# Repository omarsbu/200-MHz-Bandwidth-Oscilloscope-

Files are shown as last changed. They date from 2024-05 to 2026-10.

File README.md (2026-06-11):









**This project is intended to be an improvement on a previous version that can be seen here:**
https://github.com/omarsbu/1MHz-Bandwidth-Oscilloscope/tree/main/100kHz%20Oscilloscope

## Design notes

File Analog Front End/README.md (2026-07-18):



The purpose of an analog front end is to condition the input signal so that it maximizes the ADC’s dynamic range and limits the bandwidth to the ADC’s Nyquist frequency. Attenuators extend the measurable range by scaling down large input signals to within the appropriate voltage range and a programmable gain amplifier boosts small signals so they make full use of the ADC’s resolution. DC offsetting is also applied to bias the signal so that it fits well within the ADC’s input range. A high impedance JFET LNA buffer allows the oscilloscope input to be terminated with 1 MΩ or 50 Ω impedance.



The input stage of each channel consists of a set of relay switches to select between AC and DC coupling, as well as different attenuation levels. A compensated 1 MΩ L-pad attenuator is used for normal measurements with standard probes, while 50 Ω pi-attenuators are used for high-fidelity measurements from a 50 Ω source. Protection diodes clamp the input voltage if it exceeds the positive or negative supply rails.



The BUF802 is used in conjunction with the OPA140 to form a composite amplifier that delivers strong performance at both high and low frequencies. The BUF802, with its JFET input, provides exceptional AC performance but poor DC precision, while the OPA140 offers excellent DC precision but lacks sufficient bandwidth and slew rate for high-frequency signals. To leverage the strengths of both, the main input is AC-coupled to the BUF802, while the auxiliary input is driven by the OPA140’s DC offset circuitry. This circuitry uses a differential amplifier along with a DAC (0–5 V) and a 2.5 V reference to shift the output within a programmable range of ±2.5 V. A resistor in series with the differential amplifier output allows the DAC to modify the DC feedback network to the OPA140, which drives the BUF802 auxiliary input, thereby enabling a programmable DC offset of the input signal. To prevent the BUF802 output from exceeding the ±1 V differential input range of the LMH6518, Zener diodes are used to clamp the output to ±1 V. Additionally, a 50 Ω series resistor allows the BUF802 to drive the subsequent stages of the analog front-end signal chain as a 50 Ω source.



The ideal input condition of the LMH6518 are shown below:

The LMH6552 functions as a level shifter and single-ended to differential converter with 0 dB gain, providing a balanced differential input with a 2.5 V common-mode voltage to the LMH6518. The single-ended input to the LMH6552 is clamped to ±1 V by the BUF802, ensuring that the LMH6552’s differential output is also limited to ±1 V. The LMH6518 includes programmable bandwidth-limiting filters for anti-aliasing, and its output common-mode voltage is set to match the ADC’s common-mode voltage.









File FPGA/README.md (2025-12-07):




**Firmware Demo (Text is hard-coded for now)**



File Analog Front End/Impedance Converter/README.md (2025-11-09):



=> Impedance Converter serves as a buffer, presenting a 50GΩ input impedance and a driving the output with 50Ω output impedance. 

=> Large input impedance allows input impedance to be terminated with 1MΩ or 50Ω.

=> Composite amplifier formed with OPA140 which has high DC precision and BUF802 which has high superior AC performance. 

=> Differential Amplifier to offset output DC voltage by +/- 2.5V

=> Level shifter to drive LMH6518 with its ideal common-mode input voltage level for best performance.

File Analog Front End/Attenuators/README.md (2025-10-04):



=> Attenuators increase the input range of the scope by allowing signals with large amplitudes to be scaled down to within the ADC input range. 

=> Input range is reduced in 50 ohm mode due to larger power dissipation in the resistors. Higher power resistors can be used to increase the input range, however, physically larger resistors will have larger parasitics, which reduces high frequency performance of the 50 ohm path, which what it is intended for.







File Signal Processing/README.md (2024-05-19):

**Introduction**

  For this project, we will be interleaving two 12-bit ADCs for a total sample rate of 500 Msps and a total data rate of 6 Gbsp. The VGA controller that we are using only has a resolution of 640x480 pixels, so we 
cannot plot any more than 640 samples on the screen. The time interval in between each sample is 2 nanoseconds, therefore, 640 samples corresponds to a waveform that is 1.28 microseconds long. If the screen 
displays 10 horizontal divisions, then 1.28 us corresponds to 128 ns/div which is the highest time resolution that this oscilloscope will be capable of displaying. At this time per division setting, following the trigger event, the oscilloscope simply plots the first 640 samples from the ADCs against time on the display. In order to display longer time per division settings, additional processing on the data is needed before displaying the waveform on the screen. 

**Problem**

At the maximum time per division setting of 1 second/div, the oscilloscope would display a 10 second span of data across a screen with 10 divisions. Given the current data rate of 6 Gbps, this would require 60 
gigabits of memory to store all of the samples before processing them! Since we do not have enough memory to process all of the samples at once, we will need a buffer to process parts of the signal and then reconstruct the waveform from the segmented data. In order to do this, we will need to obtain a time-frequency representation of the signal that will provide insight to how its various frequency components change over time. We can obtain a time-frequency representation of a signal using two primary methods: the Short-Time Fourier Transform (STFT) and the Wavelet Transform

**Short-time Fourier Transform**

The STFT involves taking a fragments (windows) of the signal and performing FFTs on them to obtain the signal's frequency content during specific time intervals. By performing FFTs on isolated time segments of the signal, we can obtain a time-frequency representation which can be used to reconstruct the signal later on. This method is not perfect, however, since the width of the window creates a trade off between temporal and spectral resolution. Shorter windows increase temporal resolution but reduce frequency resolution, while longer windows increase frequency resolution but reduce temporal resolution. This is because longer periods cannot fit inside of a narrow window so low frequency information becomes more uncertain when increasing time resolution. Conversely, longer periods can fit inside of a wider window at the cost of it being less localized in time. For a given window size, this relationship is true for every frequency component.

**Wavelet Transform**

The wavelet transform is similar to the Fourier transform, except it replaces the complex exponentials with localized oscillations in time called wavelets. Specifically, our focus will center on Morlet wavelets, which are mathematically the same as a complex exponential multiplied by a Gaussian probability distribution function. By compressing (or dilating) the mother wavelet and convolving it with the input signal, the wavelet transform can be used to reveal how the different frequency components in a signal behave over time. The main advantage of the wavelet transform is that it uses a multresolution analysis (MRA) to provide good time resolution but poor frequency resolution at high frequencies and good frequency resolution but poor time resolution at low frequencies. This property makes the wavelet transform more flexible than the STFT which has uniform resolution for all frequency components. 

**Approach**

Since hardware libraries for FFTs are more readily avaiable, we will attempt to use a STFT-based approach for out MRA. The approach is straightforward: we will use filters to separate the high-frequency components from the low-frequency components and perform a STFT on the high frequency information. The window function will be a Gaussian PDF whose width will be chosen so that it provides good time resolution while keeping the frequency uncertainty negligible compared the the cutoff frequency of the high-pass filter. The lowpass filter will average in between samples to decimate the output data sequence while retaining low frequency information. FIFO buffers will be used to store chunks of samples for the STFT and averaging. The results from both of these operations will be stored in memory and called upon when reconstructing the waveform. The reconstruction will involve summing the inverse STFT with the averaged sequence so that the high-frequency components of the waveform effectively "ride on top of" of the low-frequency components. The reconstruction algorithm is summarized in the following block diagram:



**Matlab Simulation**

The Matlab script provided simulates a reconstruction of various signals by multiplying a section by a Gaussian PDF function with a standard deviation of 1 and then performing an FFT. The mean of the Gaussian PDF is shifted to isolate sections of the input signal and then perform an FFT on it. Each segment of the signal is reconstructed by performing an IFFT on the FFT result and the entire signal is reconstructed by combining all of the individual IFFTs of each segment. The following figure shows the result of running the Matlab script to simulate the reconstruction:

stft_reconstruct

**Sources**

https://users.rowan.edu/~polikar/WTtutorial.html

https://www.youtube.com/watch?v=jnxqHcObNK4

https://www.youtube.com/watch?v=ua2Fn1vkVqY&t=711s

https://www.youtube.com/watch?v=T9x2rvdhaIE

https://www.youtube.com/watch?v=I8_E1ppC3-Q

https://www.youtube.com/watch?v=hewTwm5P0Gg

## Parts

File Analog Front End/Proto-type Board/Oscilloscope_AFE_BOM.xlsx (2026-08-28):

Reference Designator | Description | Manufacturer | Manufacturer Part Number | Vendor | Vendor Part Number | Package | Unit Cost | Quantity | Total Cost
K1,K2,K3 | RELAY TELECOM DPDT 1A 5V | Aratas America LLC | G6J-2FL-Y DC5 | Digikey | Z2140-ND | SMT | 5.04 | 3 | 15.12
U1, U2 | IC OPAMP JFET 2 CIRCUIT | Texas Instruments | OPA2140AIDGKR | Digikey | 296-46321-1-ND | VSSOP-8 | 7.28 | 2 | 14.56
U3 | WIDE-BANDWIDTH, 2.3-NV/HZ, JFET | Texas Instruments | BUF802IRGTR | Digikey | 296-BUF802IRGTRCT-ND | VQFN-16 | 7.37 | 1 | 7.37
Q1,Q2,Q3 | MOSFET N-CH 60V 280MA | Diotec Semiconductor | 2N7002 | Digikey | 4878-2N7002CT-ND | SOT23-3 | 0.16 | 3 | 0.48
J1, J2 | CONN BNC RCPT R/A 50 OHM PCB | Molex | 731000105 | Digikey | WM5524-ND | BNC | 2.25 | 2 | 4.5
J3 | WR-PHD 2.54 MM DUAL SOCKET HEADER | Würth Elektronik | 61301621821 | Digikey | 732-61301621821-ND | DIP-16 | 0.7 | 1 | 0.7
D1,D2,D3 | DIODE STANDARD 75V 200MA | onsemi | 1N914BWT | Digikey | 1N914BWTCT-ND | SOD-523F | 0.17 | 3 | 0.51
D4, D5 | DIODE ARR SCHOTT 30V 200MA SOT23 | Diotec Semiconductor | BAT54C | Digikey | 4878-BAT54CCT-ND | SOT-23 | 0.16 |  | 0
D6,D7 | DIODE ZENER 6V 500MW | onsemi | SZMMSZ5233BT1G | Digikey | SZMMSZ5233BT1GOSCT-ND | SOD-123 | 0.34 | 2 | 0.68
C1,C6,C7,C8,C16,C17,C18,C19,C20,C21,C22,C23 | CAP CER 0.1UF 25V X7R 0603 | KEMET | C0603C104K3RACTU | Digikey | 399-C0603C104K3RACTUCT-ND | 0603 | 0.1 | 12 | 1.2
C2,C3 | CAP CER 10PF 25V X8R 0603 | KEMET | C0603C100J3HACTU | Digikey | 399-C0603C100J3HACTUCT-ND | 0603 | 0.1 | 2 | 0.2
C4 | CAP CER 1000PF 50V X7R 0603 | KEMET | C0603C102K5RACTU | Digikey | 399-C0603C102K5RACTUCT-ND | 0603 | 0.1 | 1 | 0.1
C5 | CAP CER 91PF 50V C0G/NP0 0603 | KEMET | C0603C910J5GACTU | Digikey | 399-C0603C910J5GACTUCT-ND | 0603 | 0.35 | 1 | 0.35
C9,C10,C11,C12,C13,C14,C15 | CAP CER 22UF 25V X5R 1210 | KEMET | C1210C226K3PACTU | Digikey | 399-C1210C226K3PACTUCT-ND | 1210 | 0.85 | 7 | 5.95
C24,C27 | CAP CER 1UF 25V X5R 0603 | KEMET | C0603C105K3PACTU | Digikey | 399-C0603C105K3PACTUCT-ND | 0603 | 0.16 | 2 | 0.32
C25 | CAP CER 56PF 25V X8R 0603 | KEMET | C0603C560M3HACTU | Digikey | 399-C0603C560M3HACTUCT-ND | 0603 | 0.1 | 1 | 0.1
C26 | CAP CER 330PF 25V X8R 0603 | KEMET | C0603C331J3HACTU | Digikey | 399-C0603C331J3HACTUCT-ND | 0603 | 0.1 | 1 | 0.1
C28 | CAP CER 100PF 25V C0G/NP0 0603 | KEMET | C0603C101K3GACTU | Digikey | 399-C0603C101K3GACTUCT-ND | 0603 | 0.12 | 1 | 0.12
R1 | RES 988K OHM 0.1% 1/10W 0603 | YAGEO | RT0603BRD07988KL | Digikey | 13-RT0603BRD07988KLCT-ND | 0603 | 0.1 | 1 | 0.1
R2,R24,R25 | RES 10K OHM 1% 1/10W 0603 | YAGEO | RC0603FR-1010KL | Digikey | 13-RC0603FR-1010KLCT-ND | 0603 | 0.1 | 3 | 0.3
R3 | RES 898K OHM 0.5% 1/10W 0603 | KOA Speer Electronics, Inc. | RN73H1JTTD8983D50 | Digikey | 2019-RN73H1JTTD8983D50CT-ND | 0603 | 0.1 | 1 | 0.1
R4 | RES 100K OHM 1% 1/10W 0603 | YAGEO | RC0603FR-07100KL | Digikey | 311-100KHRCT-ND | 0603 | 0.1 | 1 | 0.1
R5,R7 | RES 75 OHM 1% 1/10W 0603 | YAGEO | RC0603FR-0775RL | Digikey | 311-75.0HRCT-ND | 0603 | 0.1 | 2 | 0.2
R6 | RES 120 OHM 5% 1/10W 0603 | YAGEO | RC0603JR-07120RL | Digikey | 311-120GRCT-ND | 0603 | 0.1 | 1 | 0.1
R8,R9,R10 | RES 10 OHM 1% 1/10W 0603 | Stackpole Electronics Inc | RMCF0603FT10R0CT-ND | Digikey | RMCF0603FT10R0CT-ND | 0603 | 0.1 | 3 | 0.3
R11,R20 | RES 1K OHM 1% 1/10W 0603 | YAGEO | RC0603FR-071KL | Digikey | 311-1.00KHRCT-ND | 0603 | 0.1 | 2 | 0.2
R12,R16,R17,R18 | RES SMD 499K OHM 0.1% 1/10W 0603 | YAGEO | RT0603BRD07499KL | Digikey | YAG4565CT-ND | 0603 | 0.1 | 4 | 0.4
R13 | RES 835K OHM 1% 1/10W 0603 | KOA Speer Electronics, Inc. | RN73H1JTTD8353F25 | Digikey | 2019-RN73H1JTTD8353F25CT-ND | 0603 | 0.13 | 1 | 0.13
R14 | RES 165K OHM 1% 1/10W 0603 | YAGEO | RC0603FR-07165KL | Digikey | 311-165KHRCT-ND | 0603 | 0.1 | 1 | 0.1
R15,R26 | RES 80K OHM 0.1% 0.15W 0603 | Vishay Dale Thin Film | PTN0603E8002BST1 | Digikey | 764-1457-1-ND | 0603 | 0.74 | 2 | 1.48
R19 | RES 30 OHM 5% 1/10W 0603 | YAGEO | RC0603JR-0730RL | Digikey | 311-30GRCT-ND | 0603 | 0.1 | 1 | 0.1
R21 | RES 2K OHM 1% 1/10W 0603 | YAGEO | RC0603FR-072KL | Digikey | 311-2.00KHRCT-ND | 0603 | 0.1 | 1 | 0.1
R22 | RES 17.8K OHM 1% 1/10W 0603 | YAGEO | RC0603FR-0717K8L | Digikey | 311-17.8KHRCT-ND | 0603 | 0.1 | 1 | 0.1
R23 | RES 10M OHM 1% 1/10W 0603 | YAGEO | RC0603FR-0710ML | Digikey | 311-10.0MHRCT-ND | 0603 | 0.1 | 1 | 0.1
R27 | RES 20K OHM 1% 1/10W 0603 | YAGEO | RC0603FR-0720KL | Digikey | 311-20.0KHRCT-ND | 0603 | 0.1 | 1 | 0.1
R28 | RES 50 OHM 0.1% 1/10W 0603 | YAGEO | RT0603BRD0750RL | Digikey | 13-RT0603BRD0750RLCT-ND | 0603 | 0.1 | 1 | 0.1
 |  |  |  |  |  |  |  |  | 56.47

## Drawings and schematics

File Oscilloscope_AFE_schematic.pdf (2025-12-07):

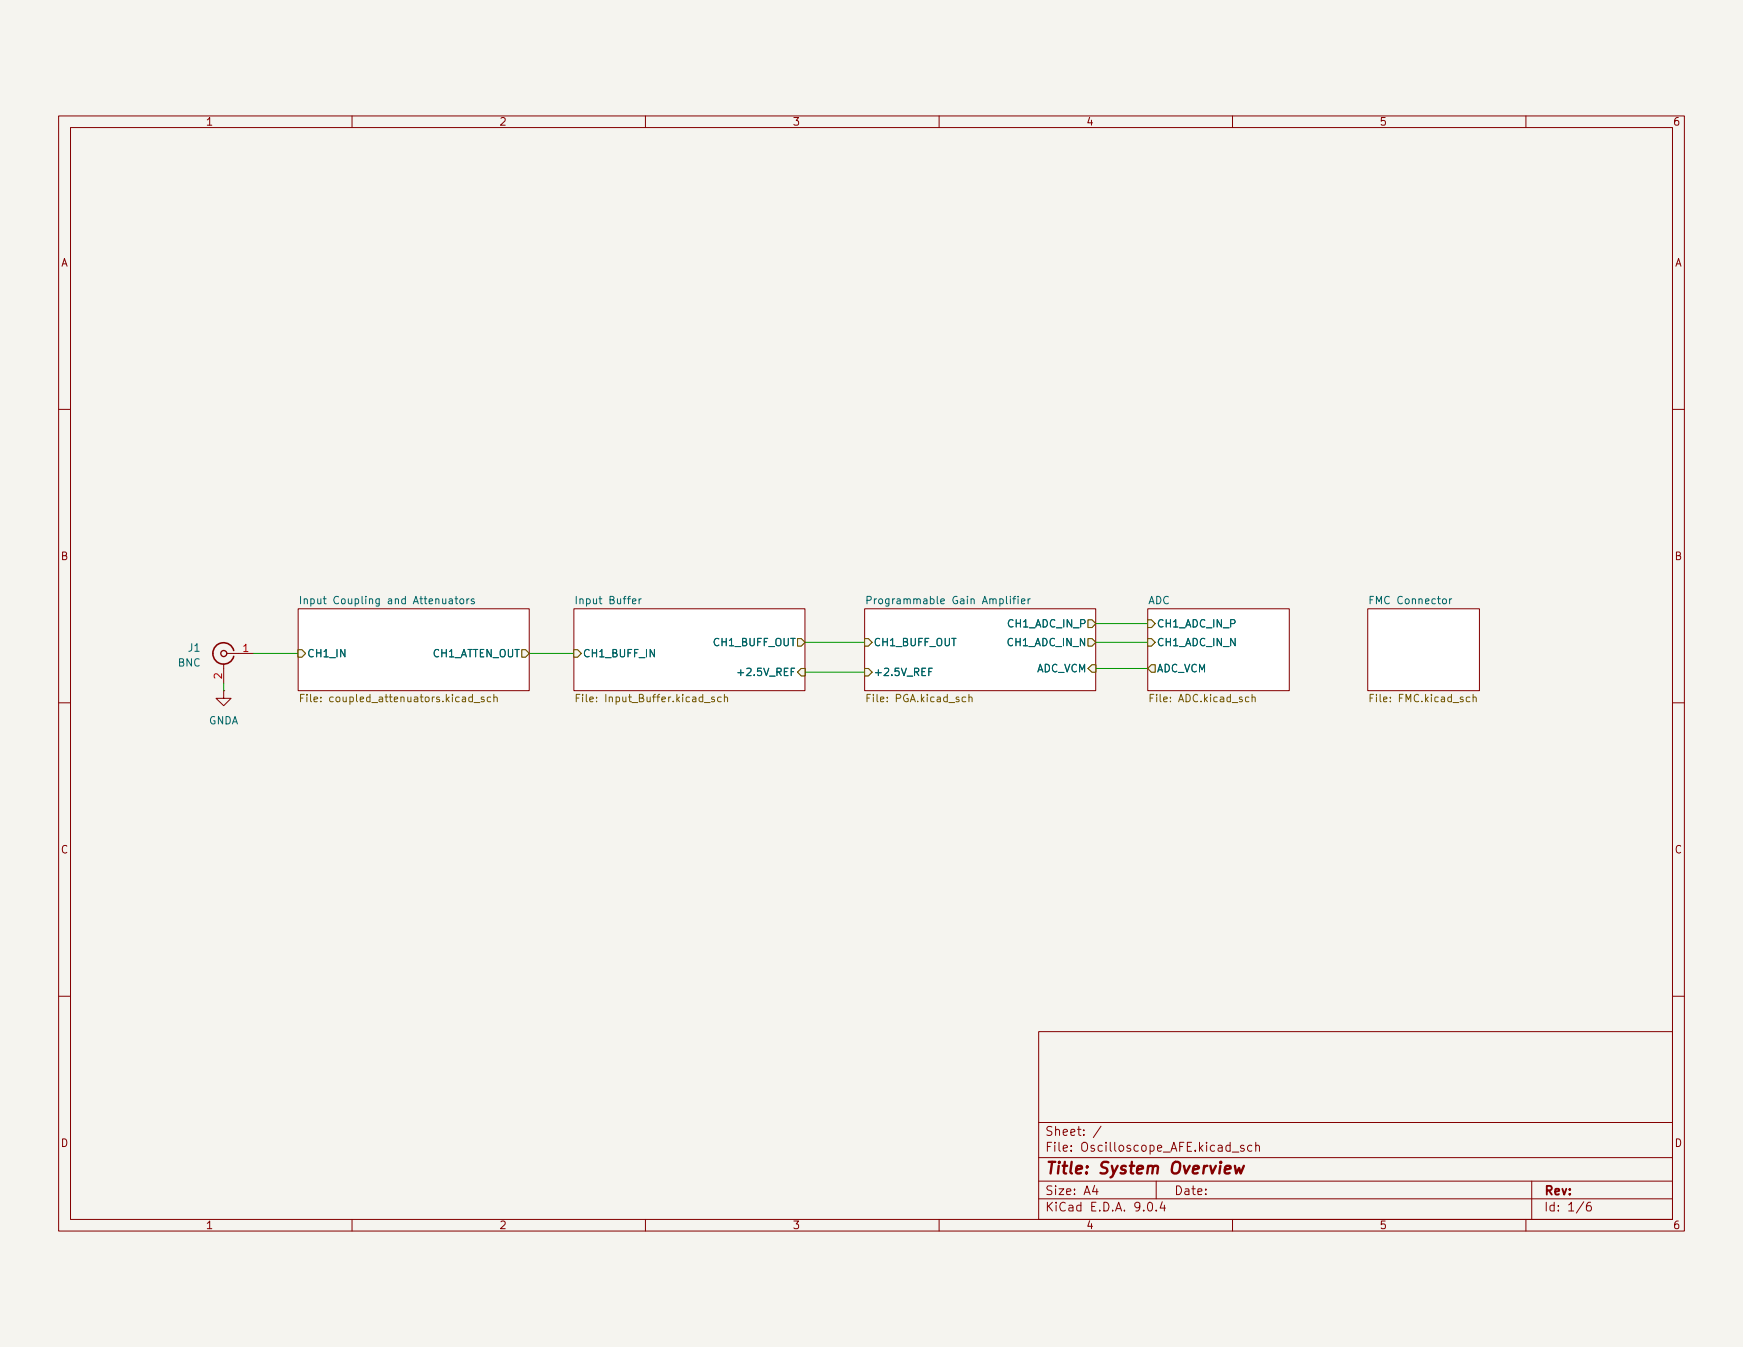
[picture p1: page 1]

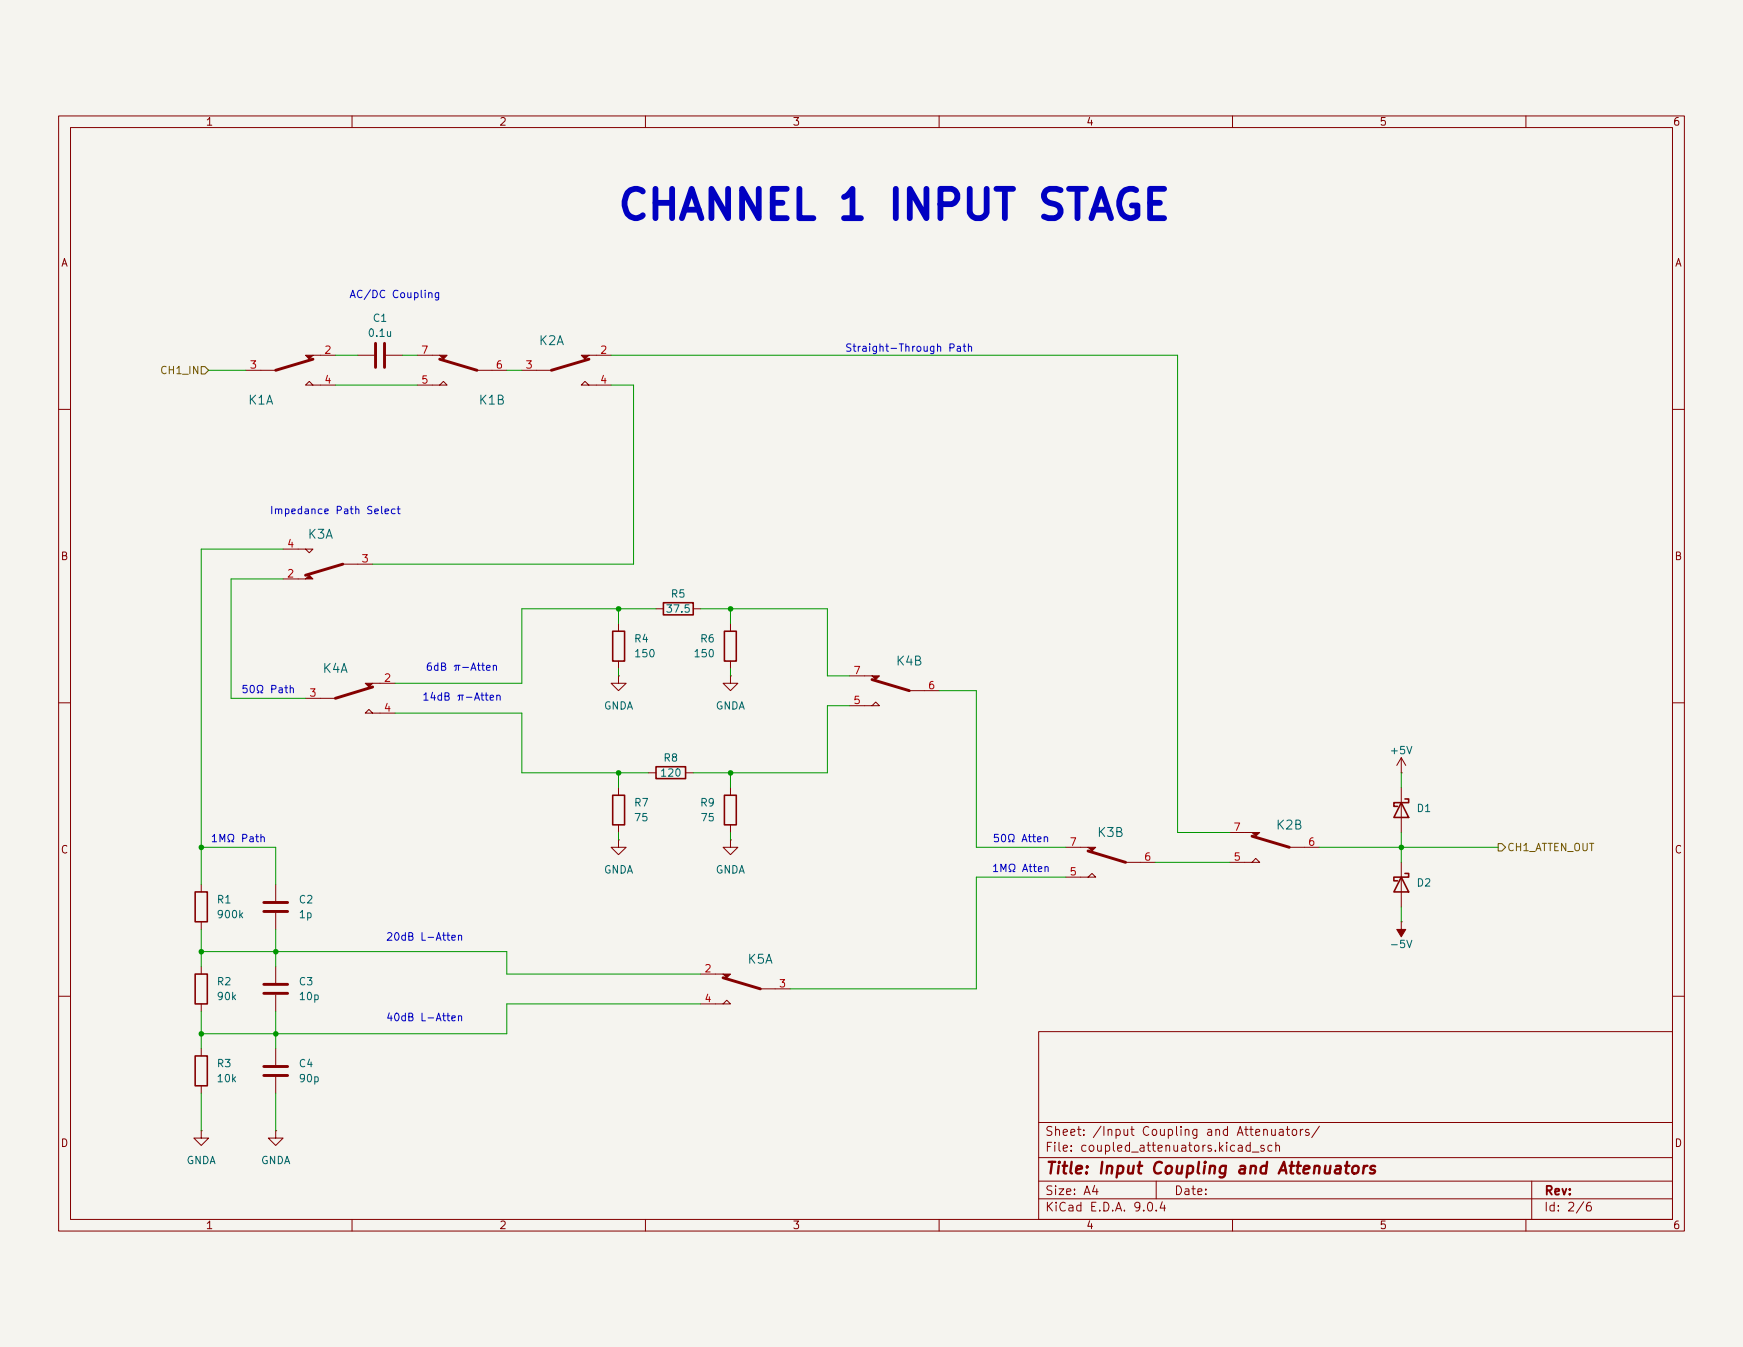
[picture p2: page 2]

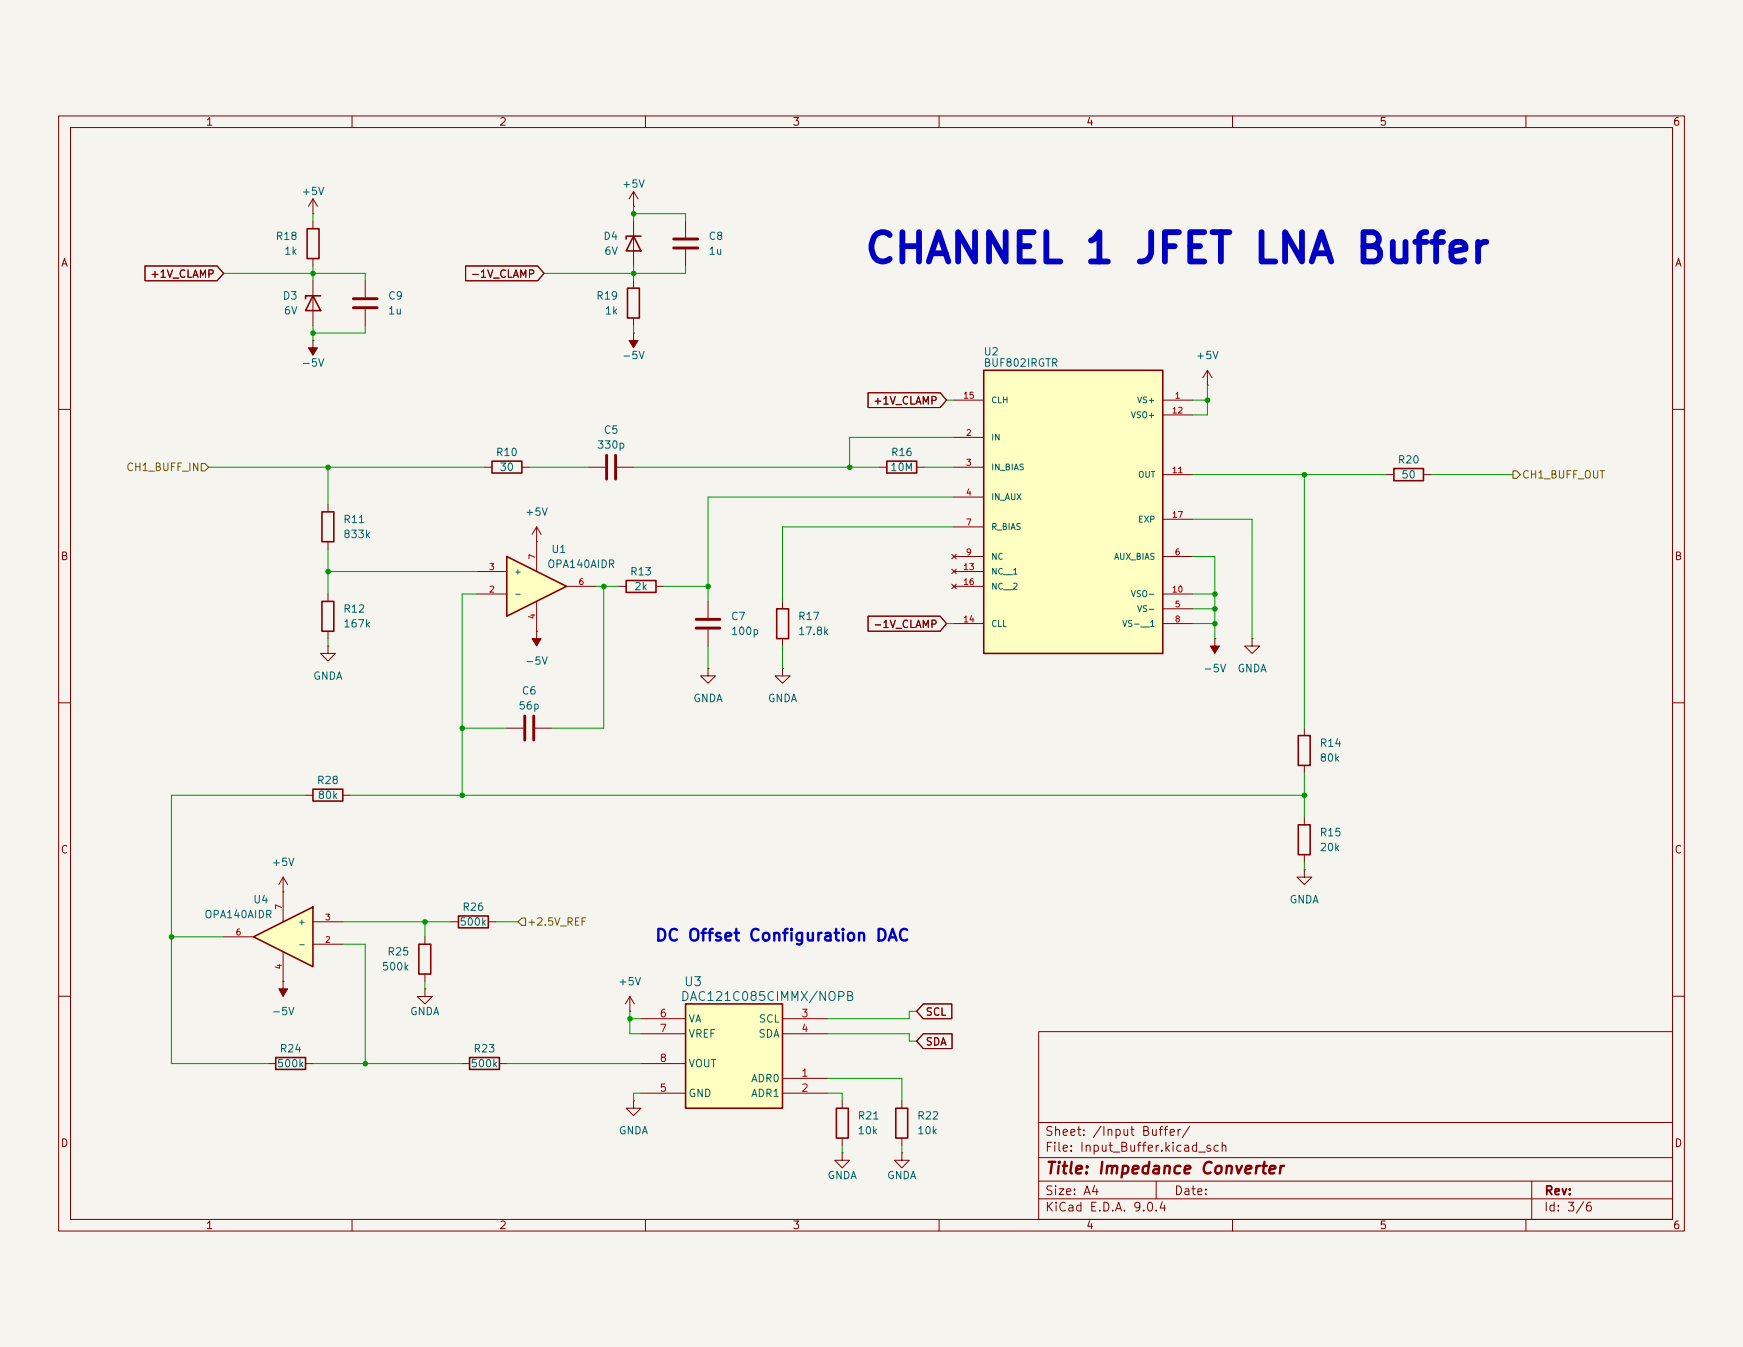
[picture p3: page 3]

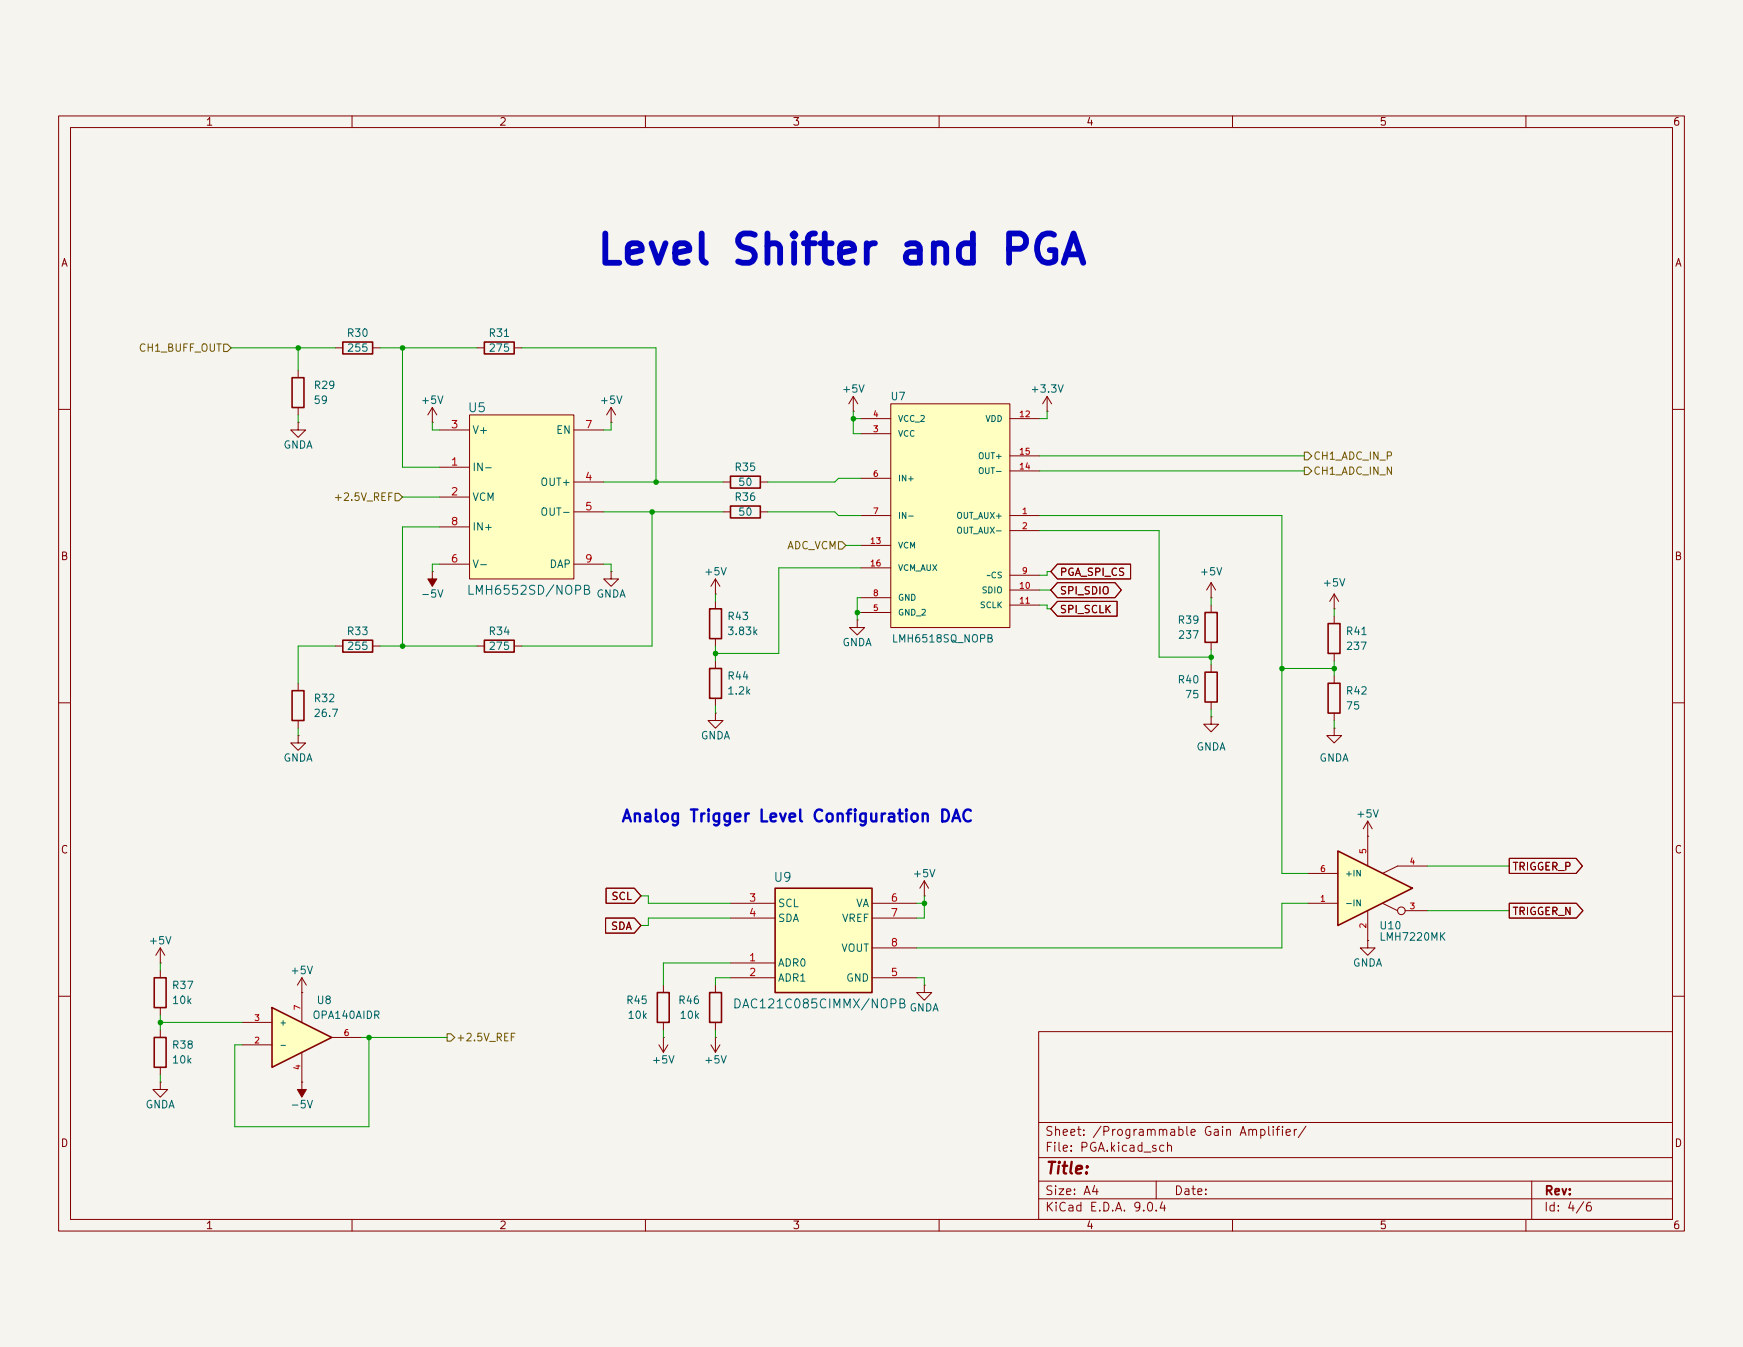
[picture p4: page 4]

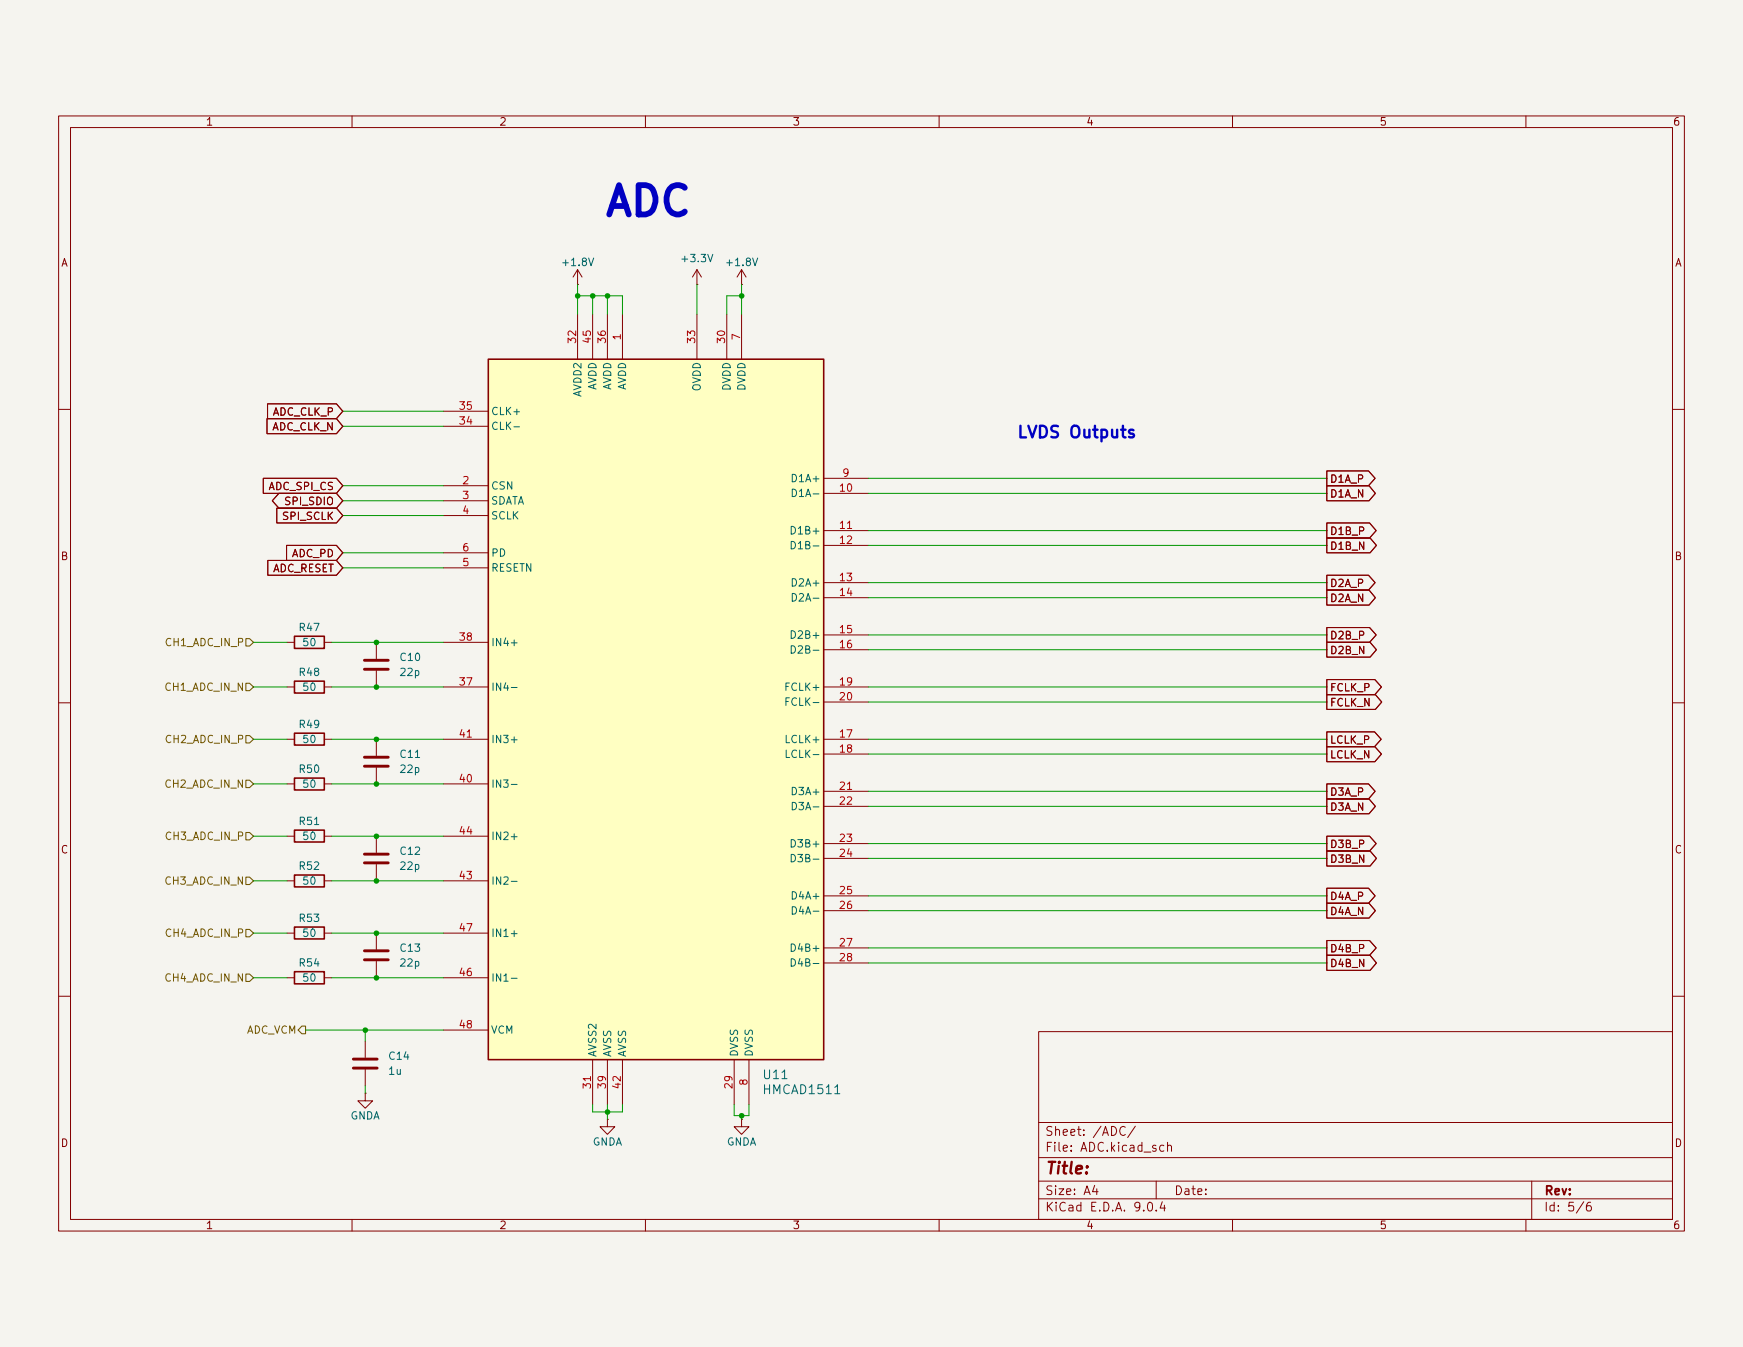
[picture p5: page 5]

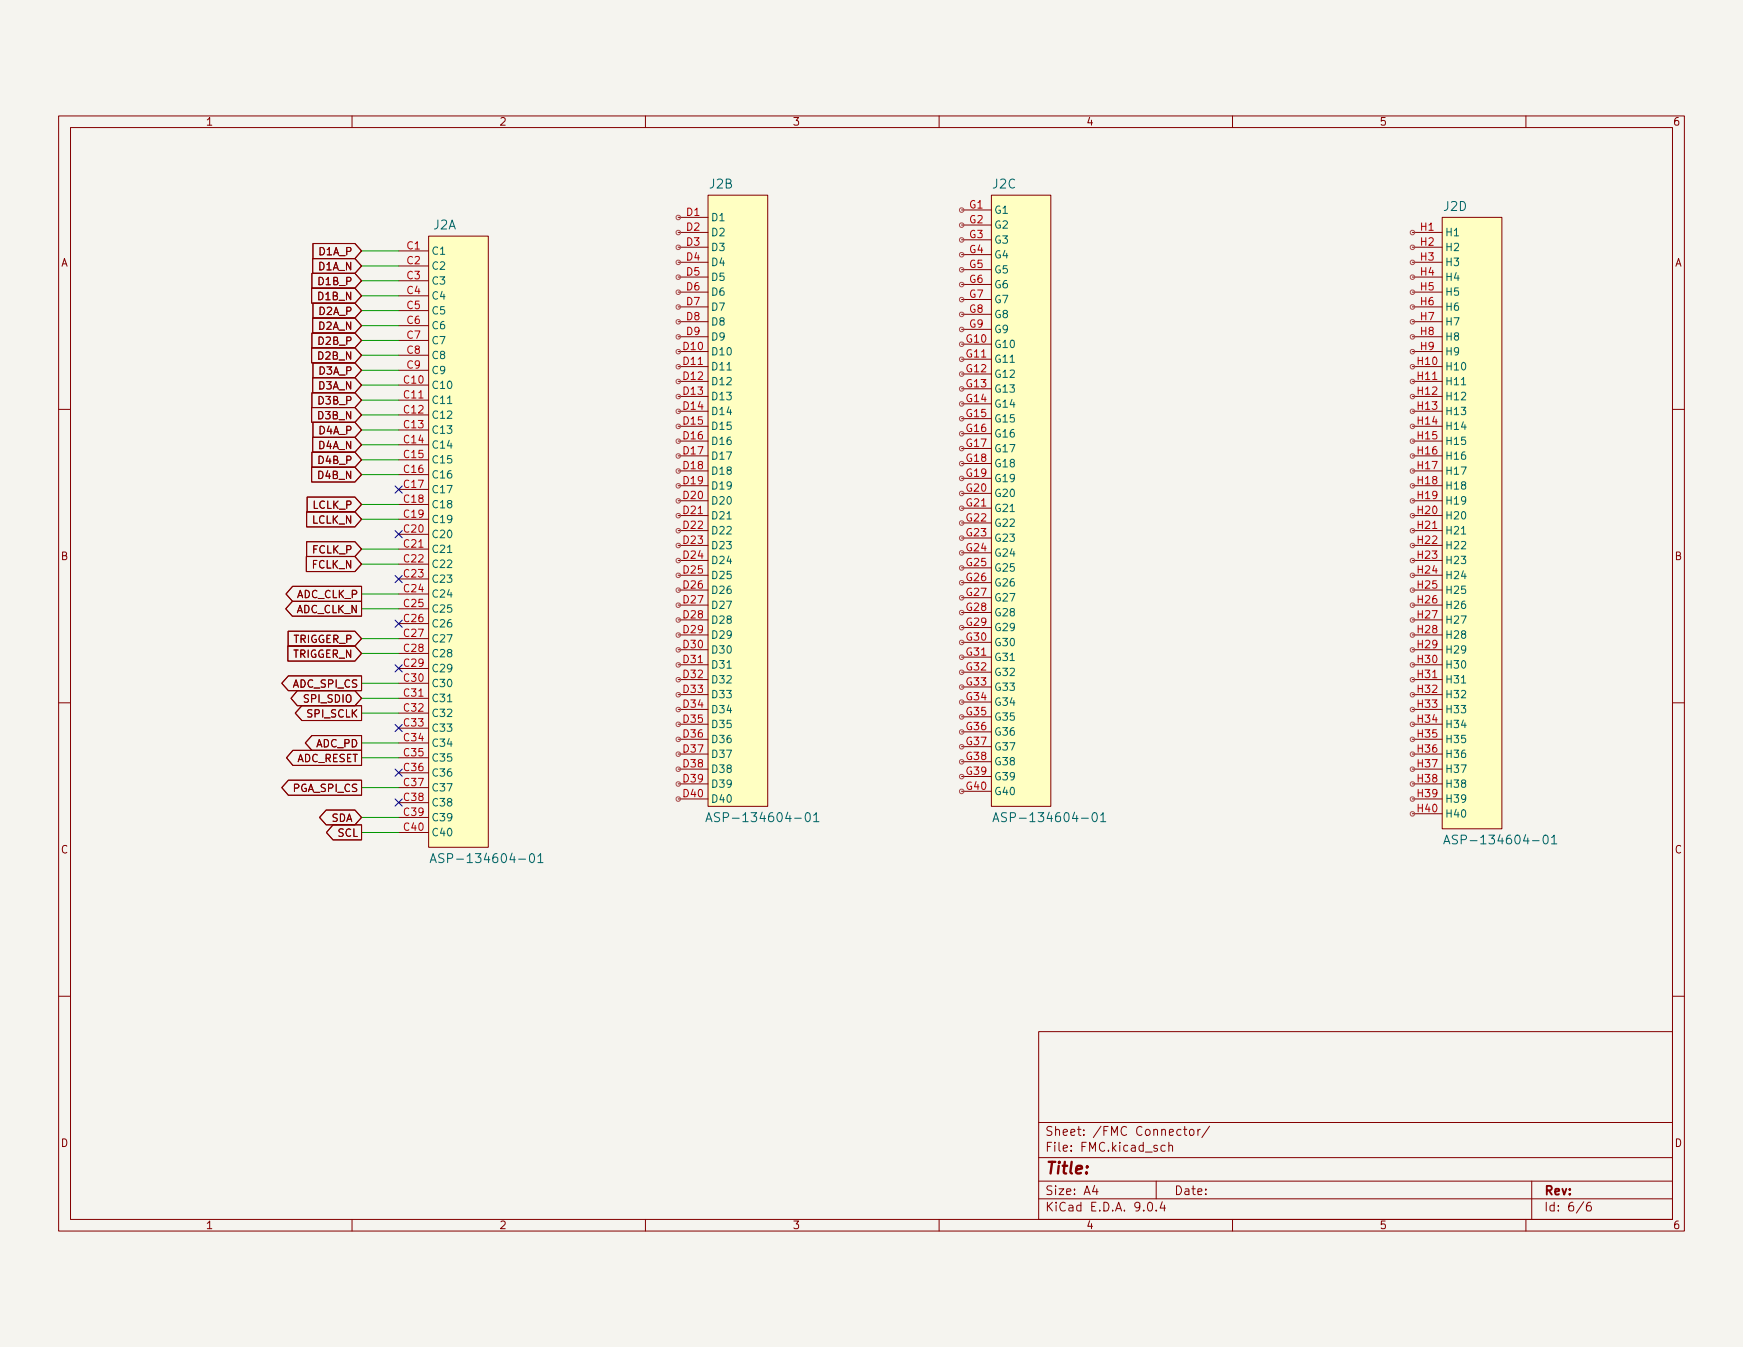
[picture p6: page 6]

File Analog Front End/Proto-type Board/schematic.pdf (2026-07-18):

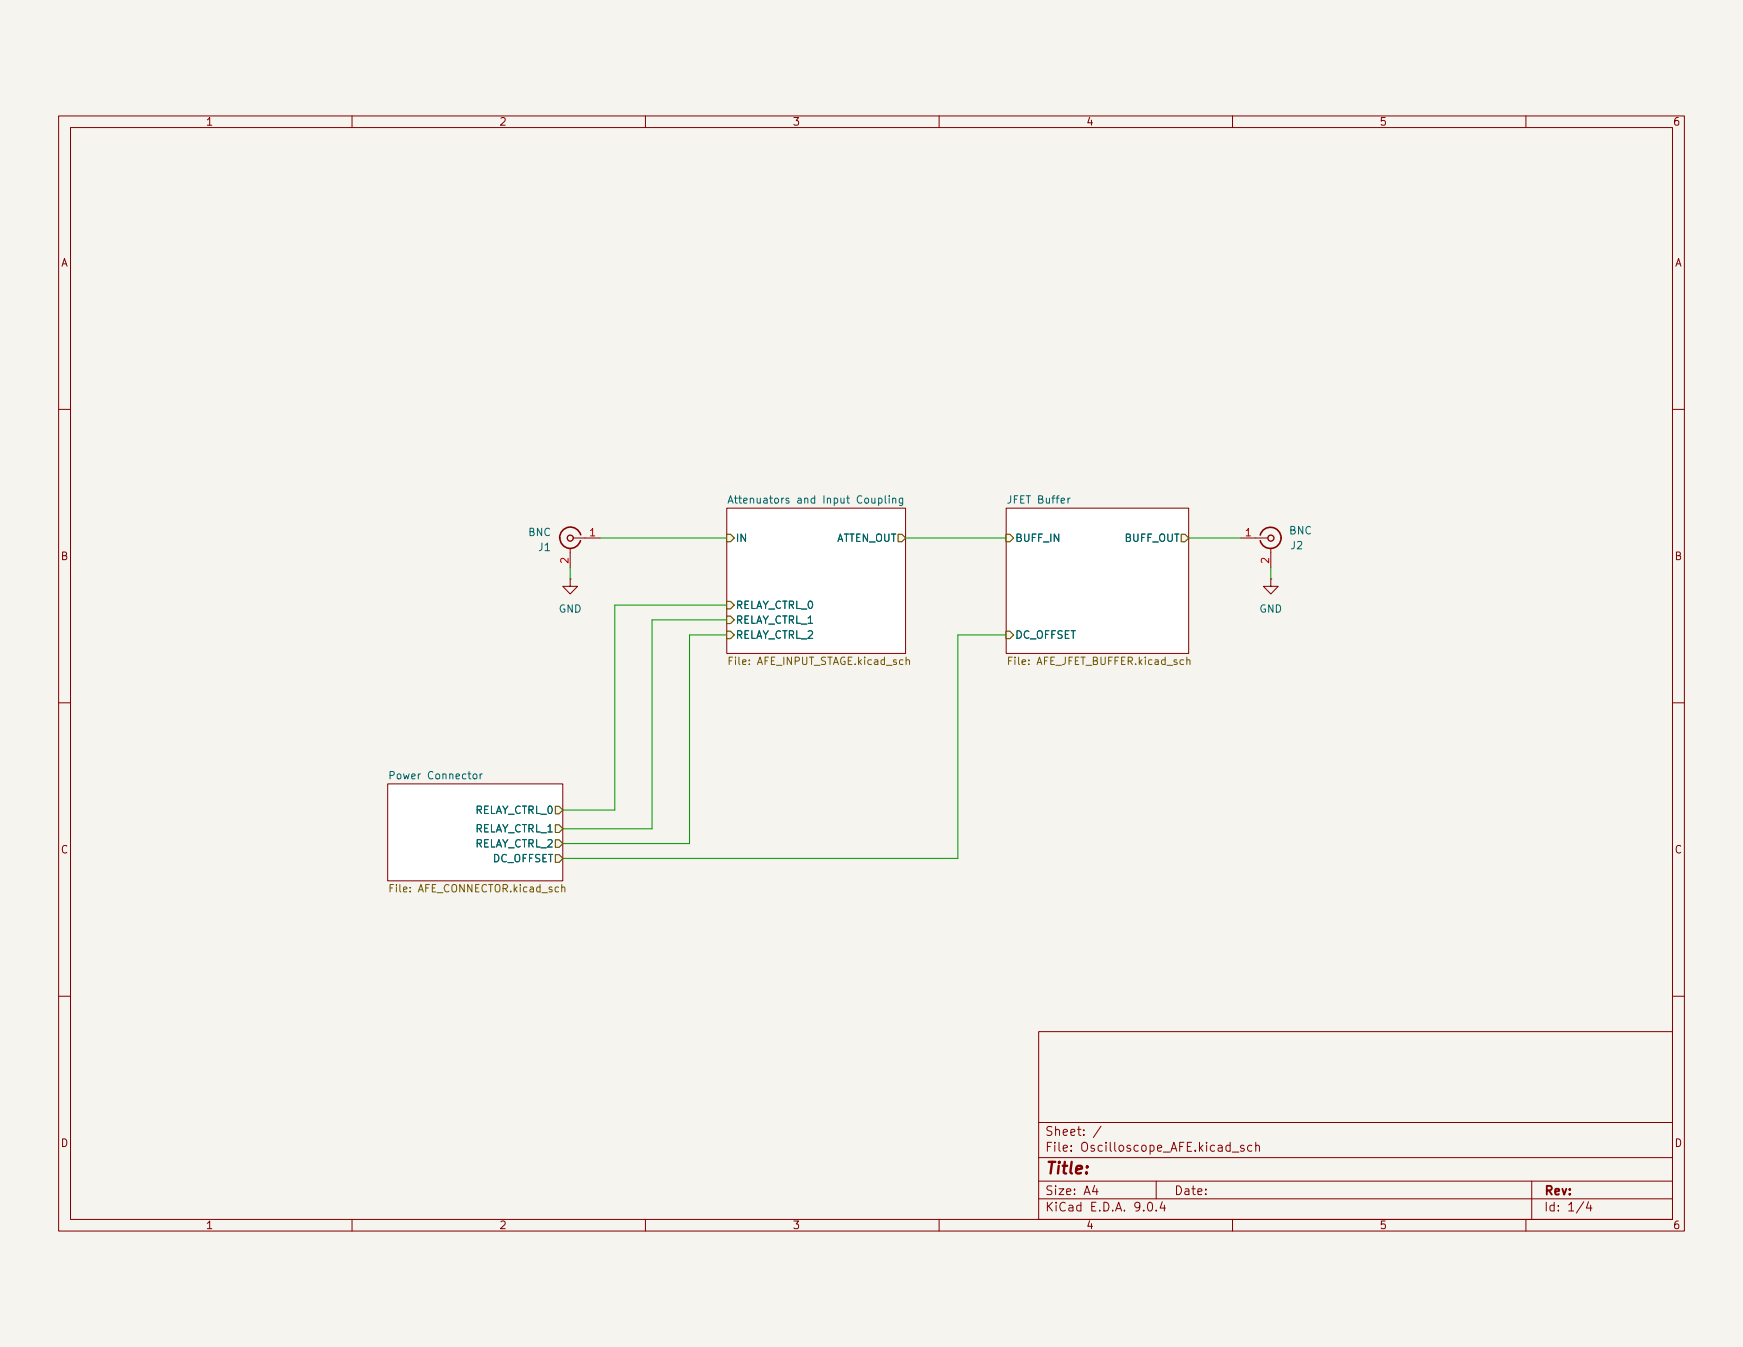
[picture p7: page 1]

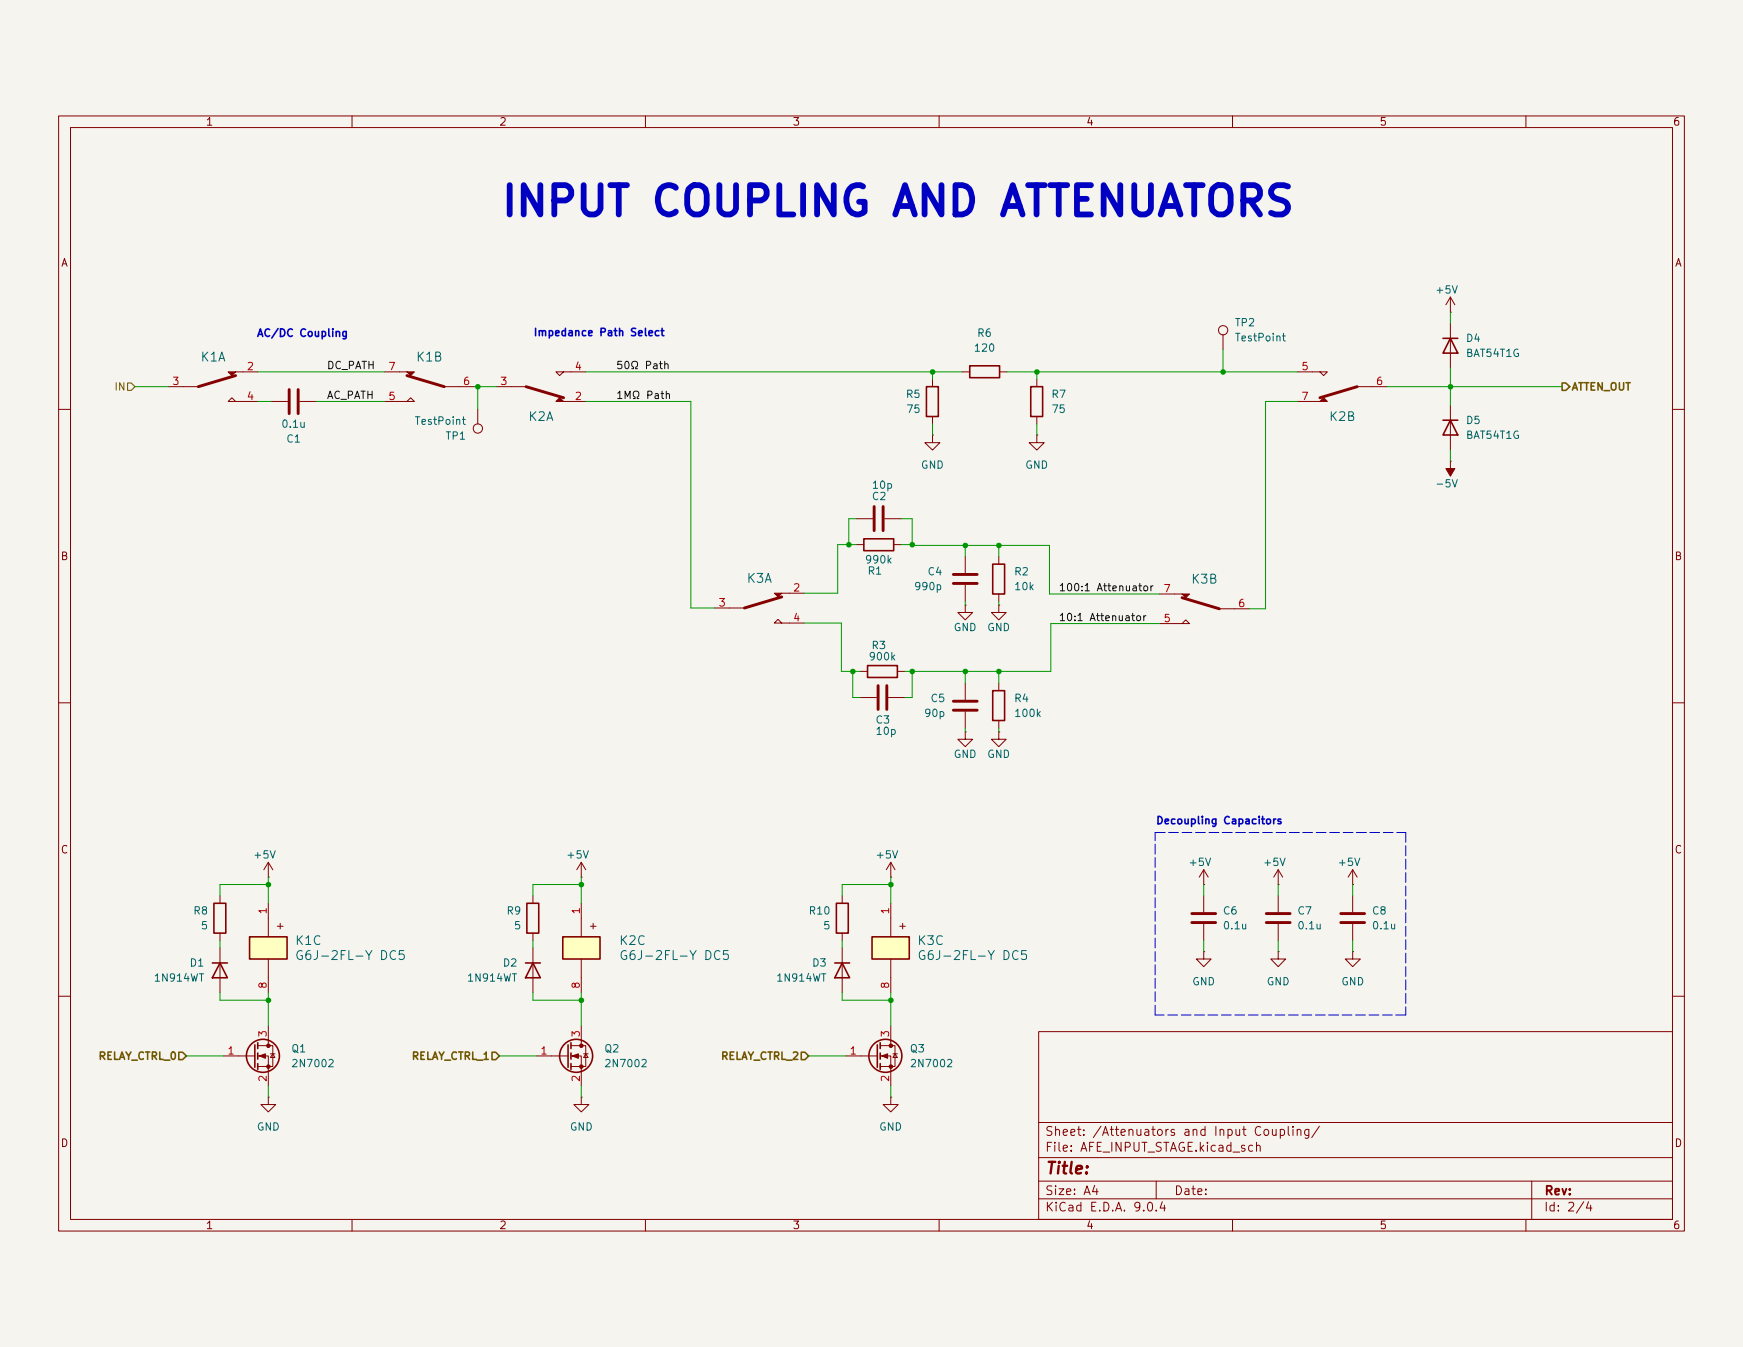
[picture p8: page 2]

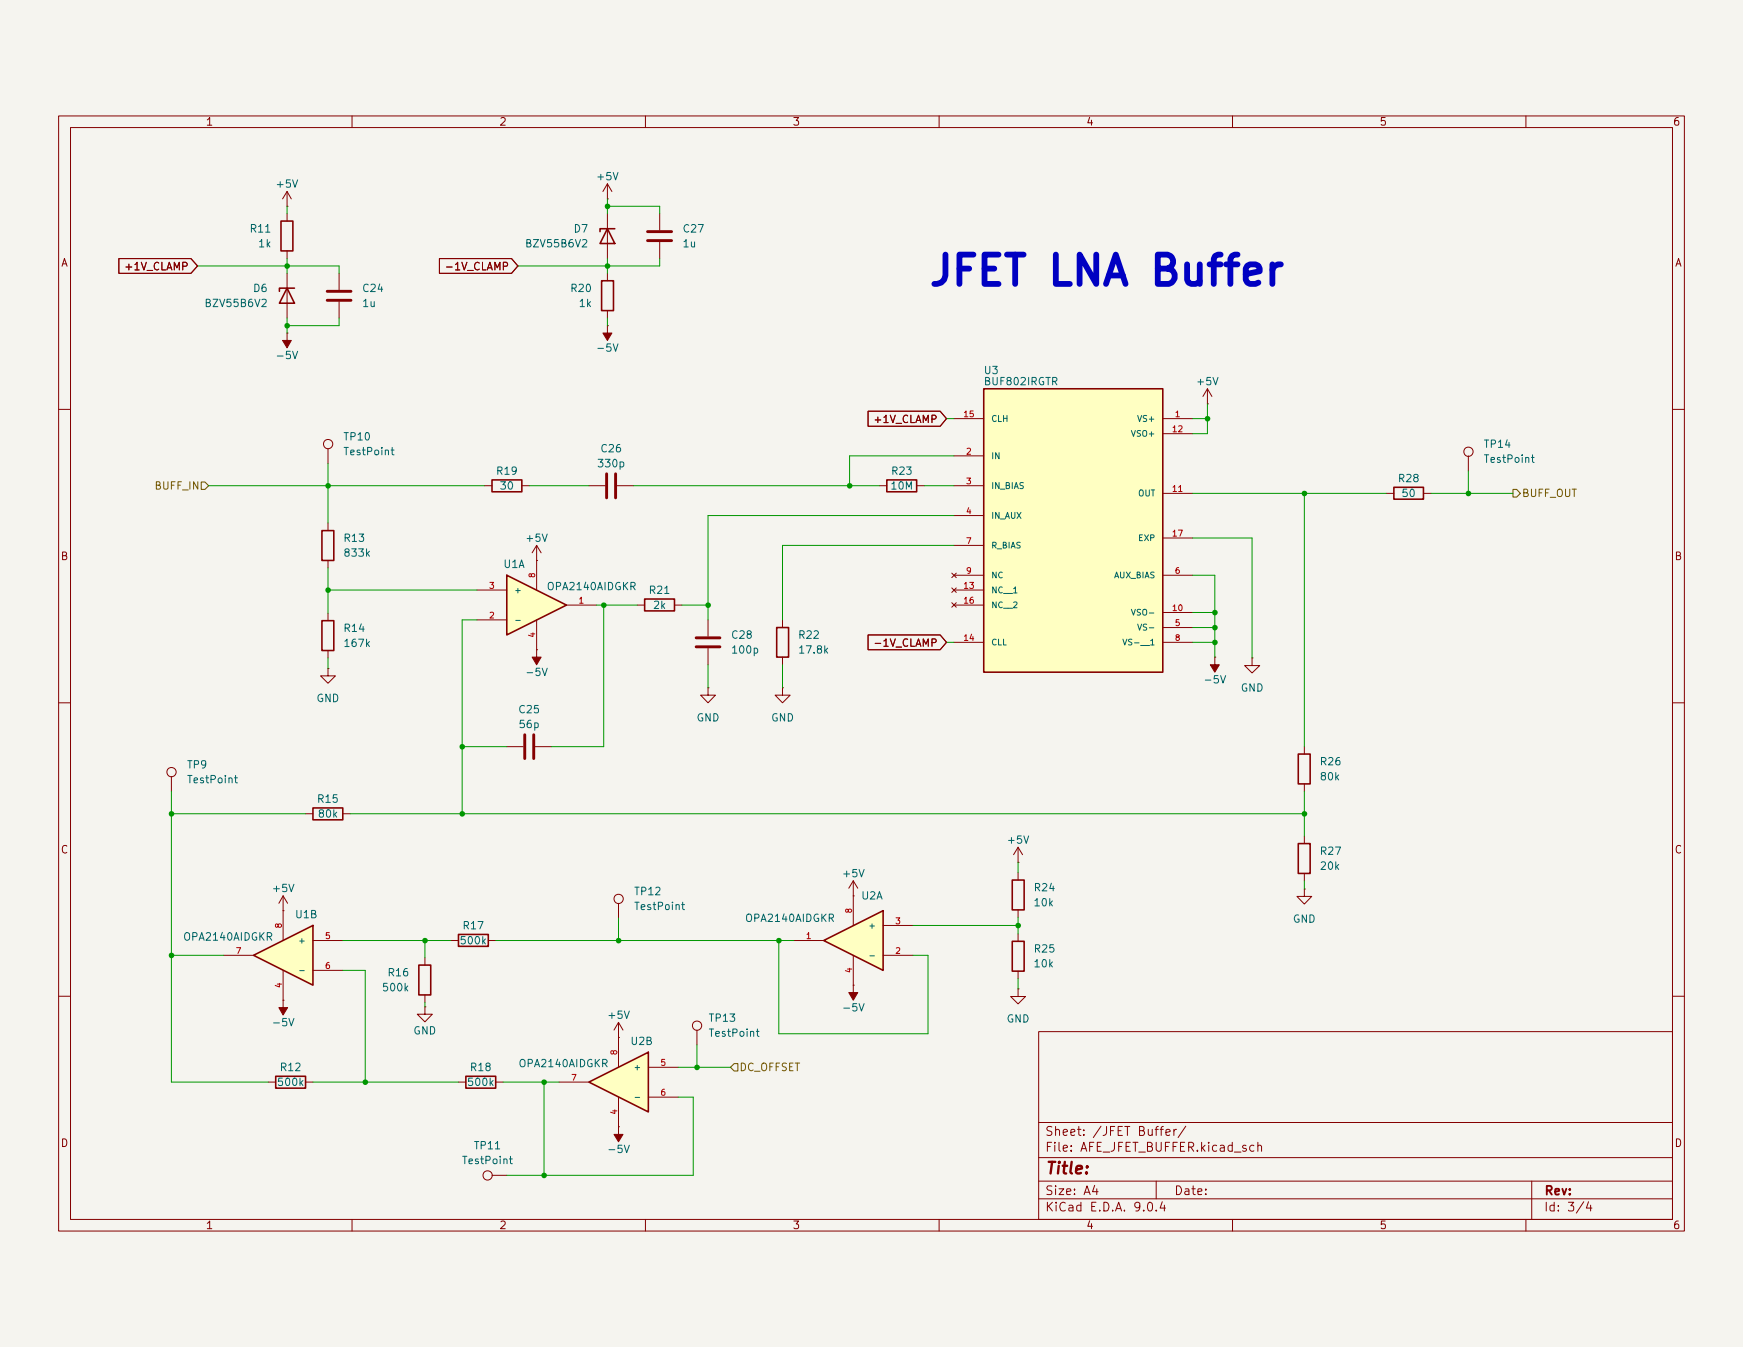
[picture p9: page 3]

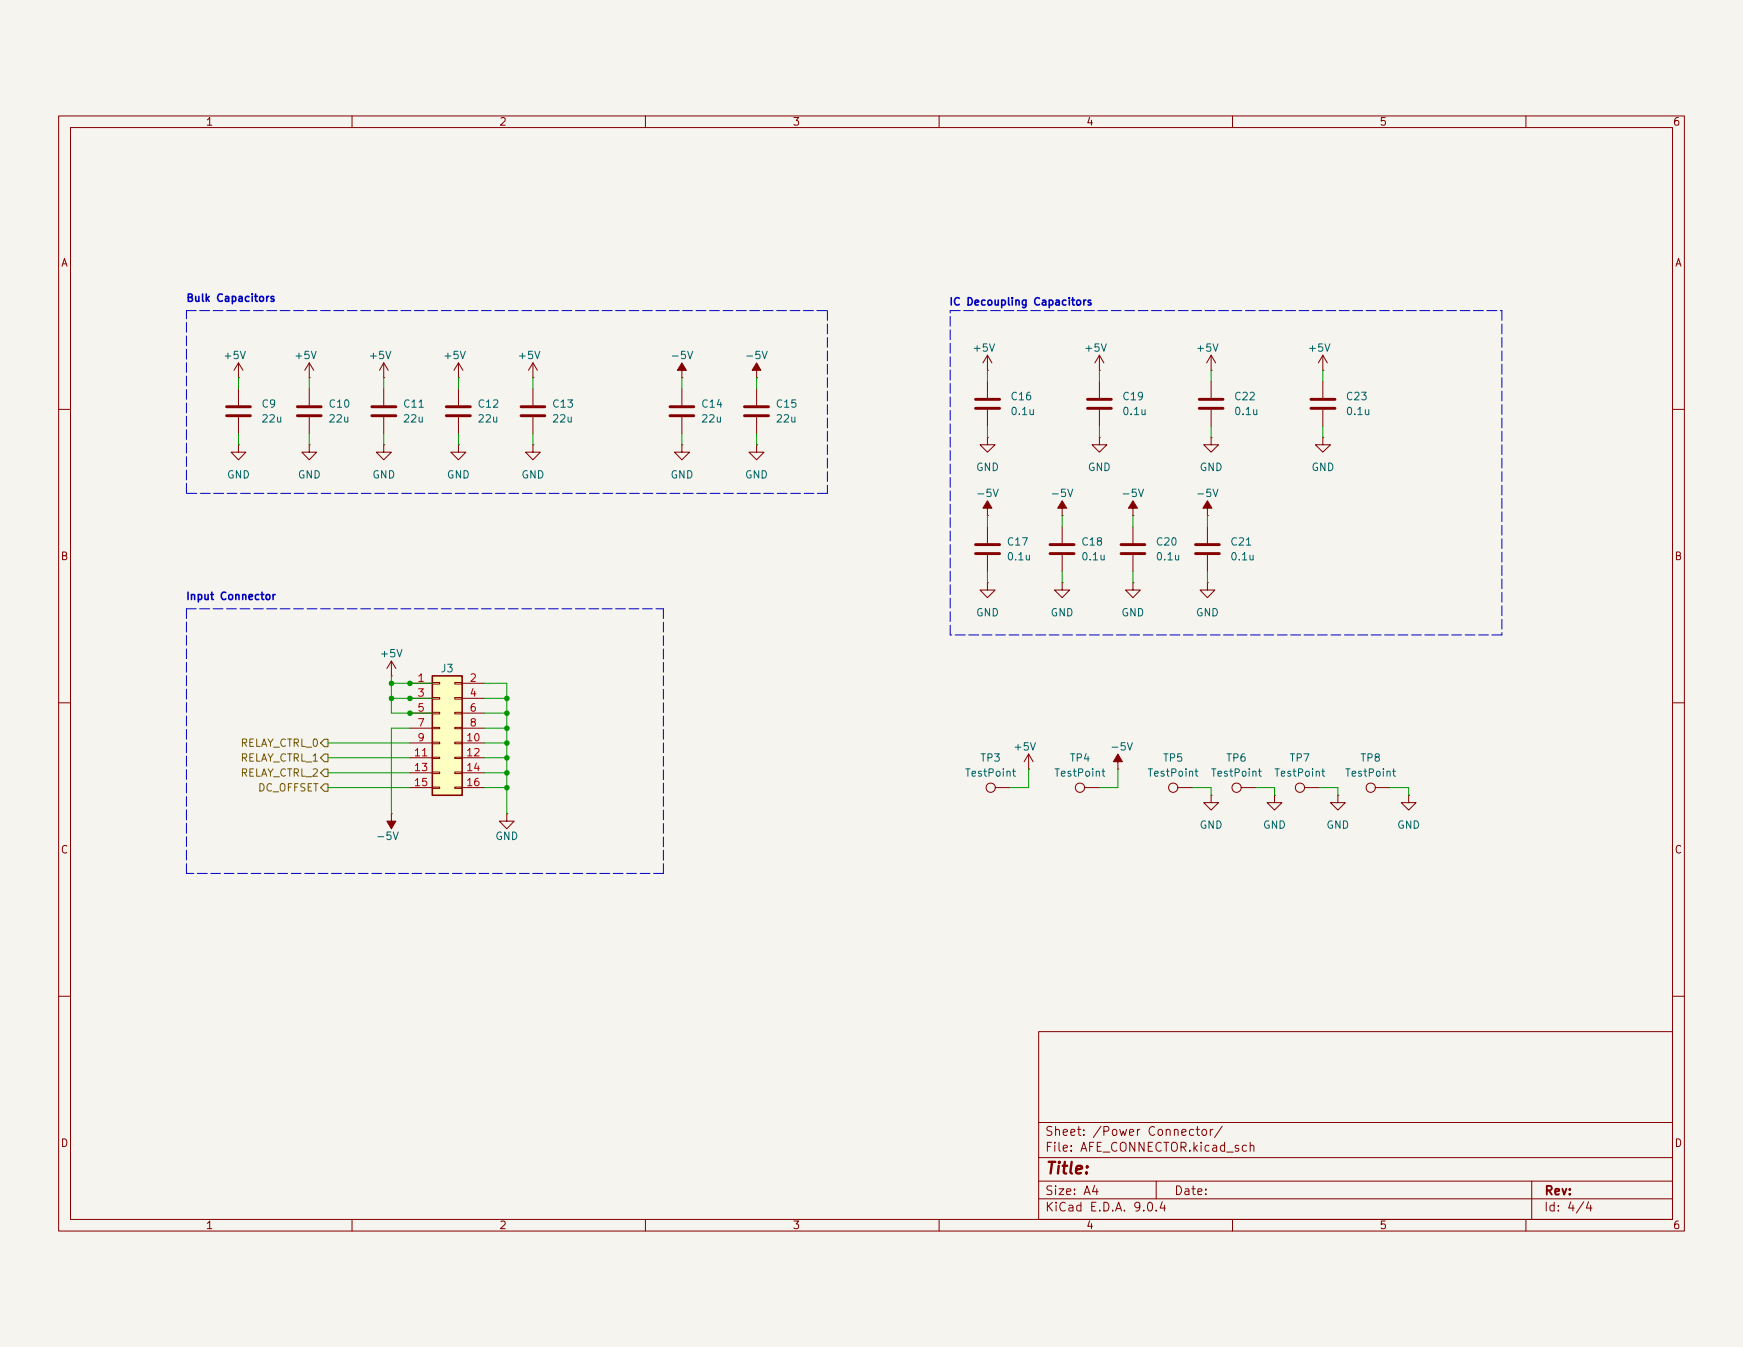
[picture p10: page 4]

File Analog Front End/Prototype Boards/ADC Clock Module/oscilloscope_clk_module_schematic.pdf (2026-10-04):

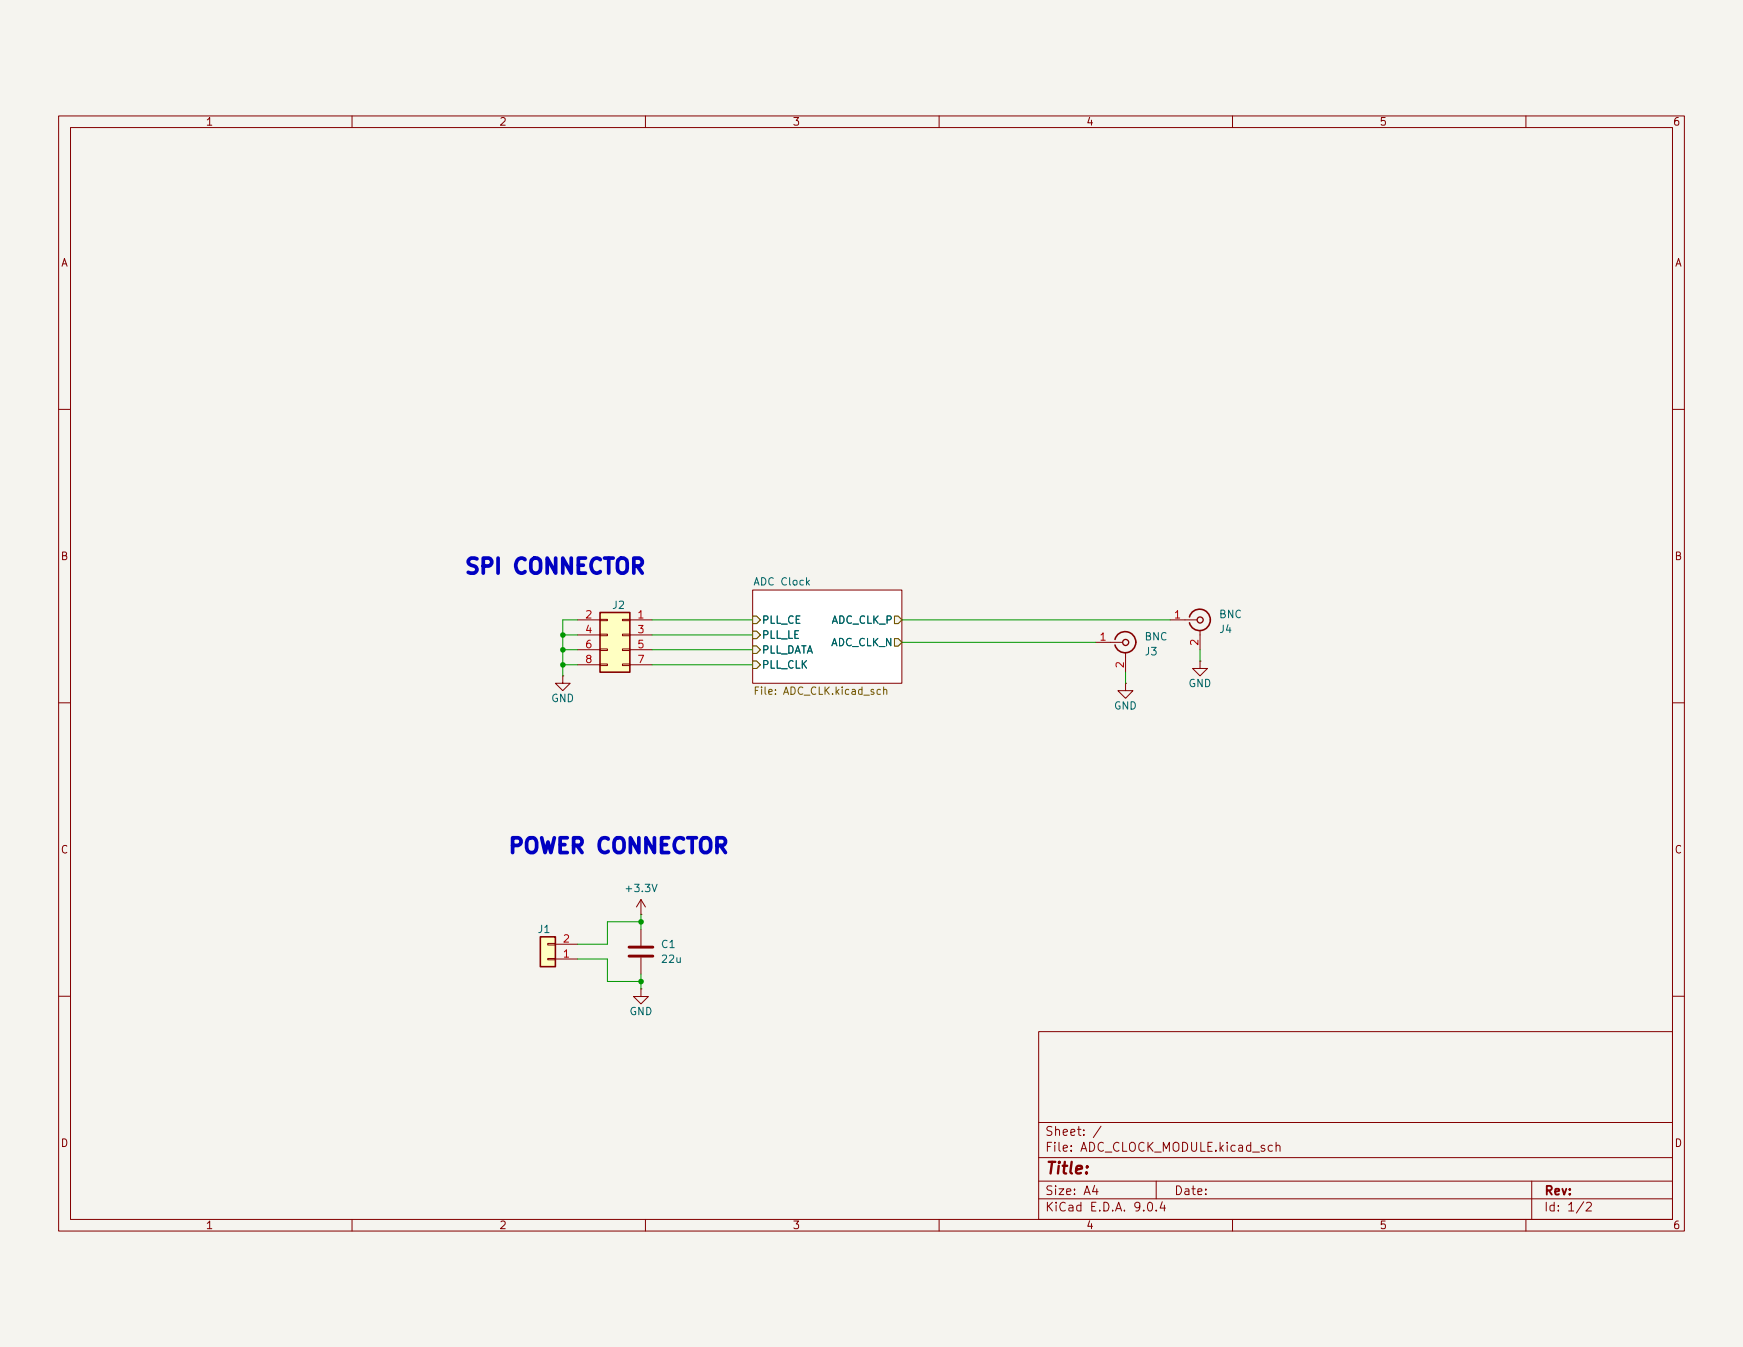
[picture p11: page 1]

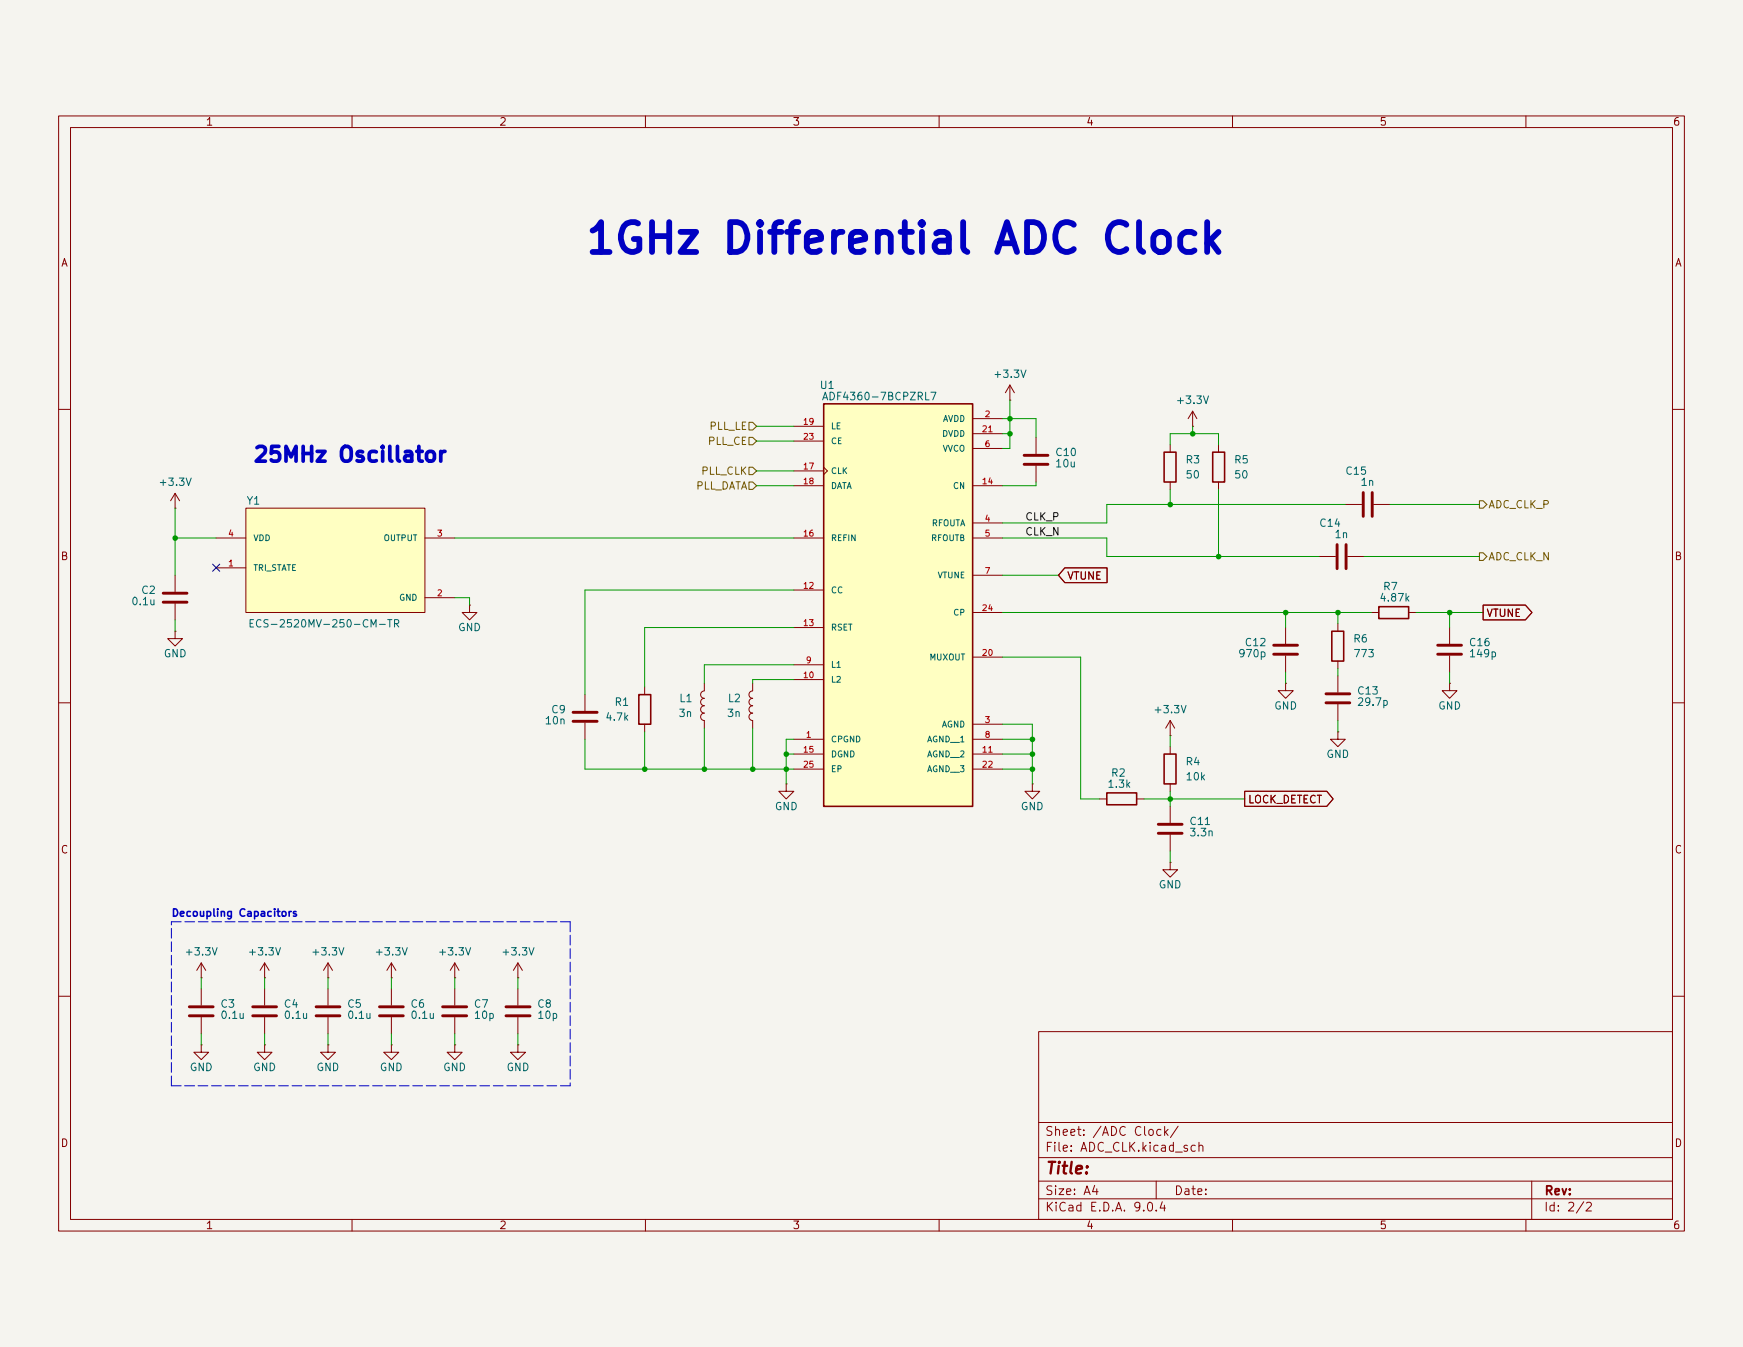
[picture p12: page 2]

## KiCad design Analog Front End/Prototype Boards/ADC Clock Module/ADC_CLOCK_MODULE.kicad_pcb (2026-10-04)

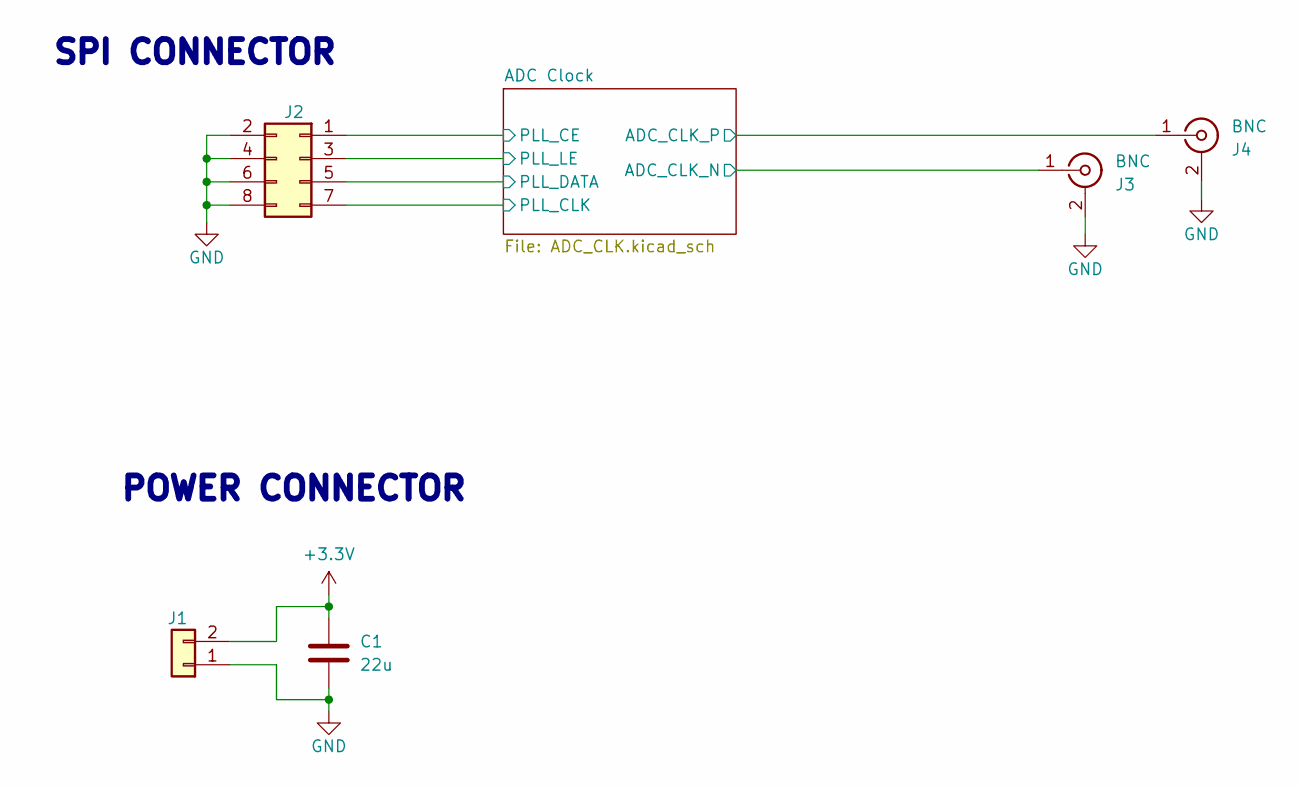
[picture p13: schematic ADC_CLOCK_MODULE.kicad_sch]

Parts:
C1: 22u; C_1210_3225Metric_Pad1.33x2.70mm_HandSolder
J1: Conn_01x02; PinHeader_1x02_P2.54mm_Vertical
J2: Conn_02x04_Odd_Even; PinHeader_2x04_P2.54mm_Vertical
J3, J4: BNC; SMA_Amphenol_132289_EdgeMount

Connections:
+3.3V: C1.1, J1.2; also elsewhere on the board
/ADC Clock/ADC_CLK_N: J3.1 (In); also elsewhere on the board
/ADC Clock/ADC_CLK_P: J4.1 (In); also elsewhere on the board
/ADC Clock/PLL_CE: J2.1; also elsewhere on the board
/ADC Clock/PLL_CLK: J2.7; also elsewhere on the board
/ADC Clock/PLL_DATA: J2.5; also elsewhere on the board
/ADC Clock/PLL_LE: J2.3; also elsewhere on the board
GND: C1.2, J1.1, J2.2, J2.4, J2.6, J2.8, J3.2 (Ext), J4.2 (Ext); also elsewhere on the board

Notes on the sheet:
SPI CONNECTOR
POWER CONNECTOR

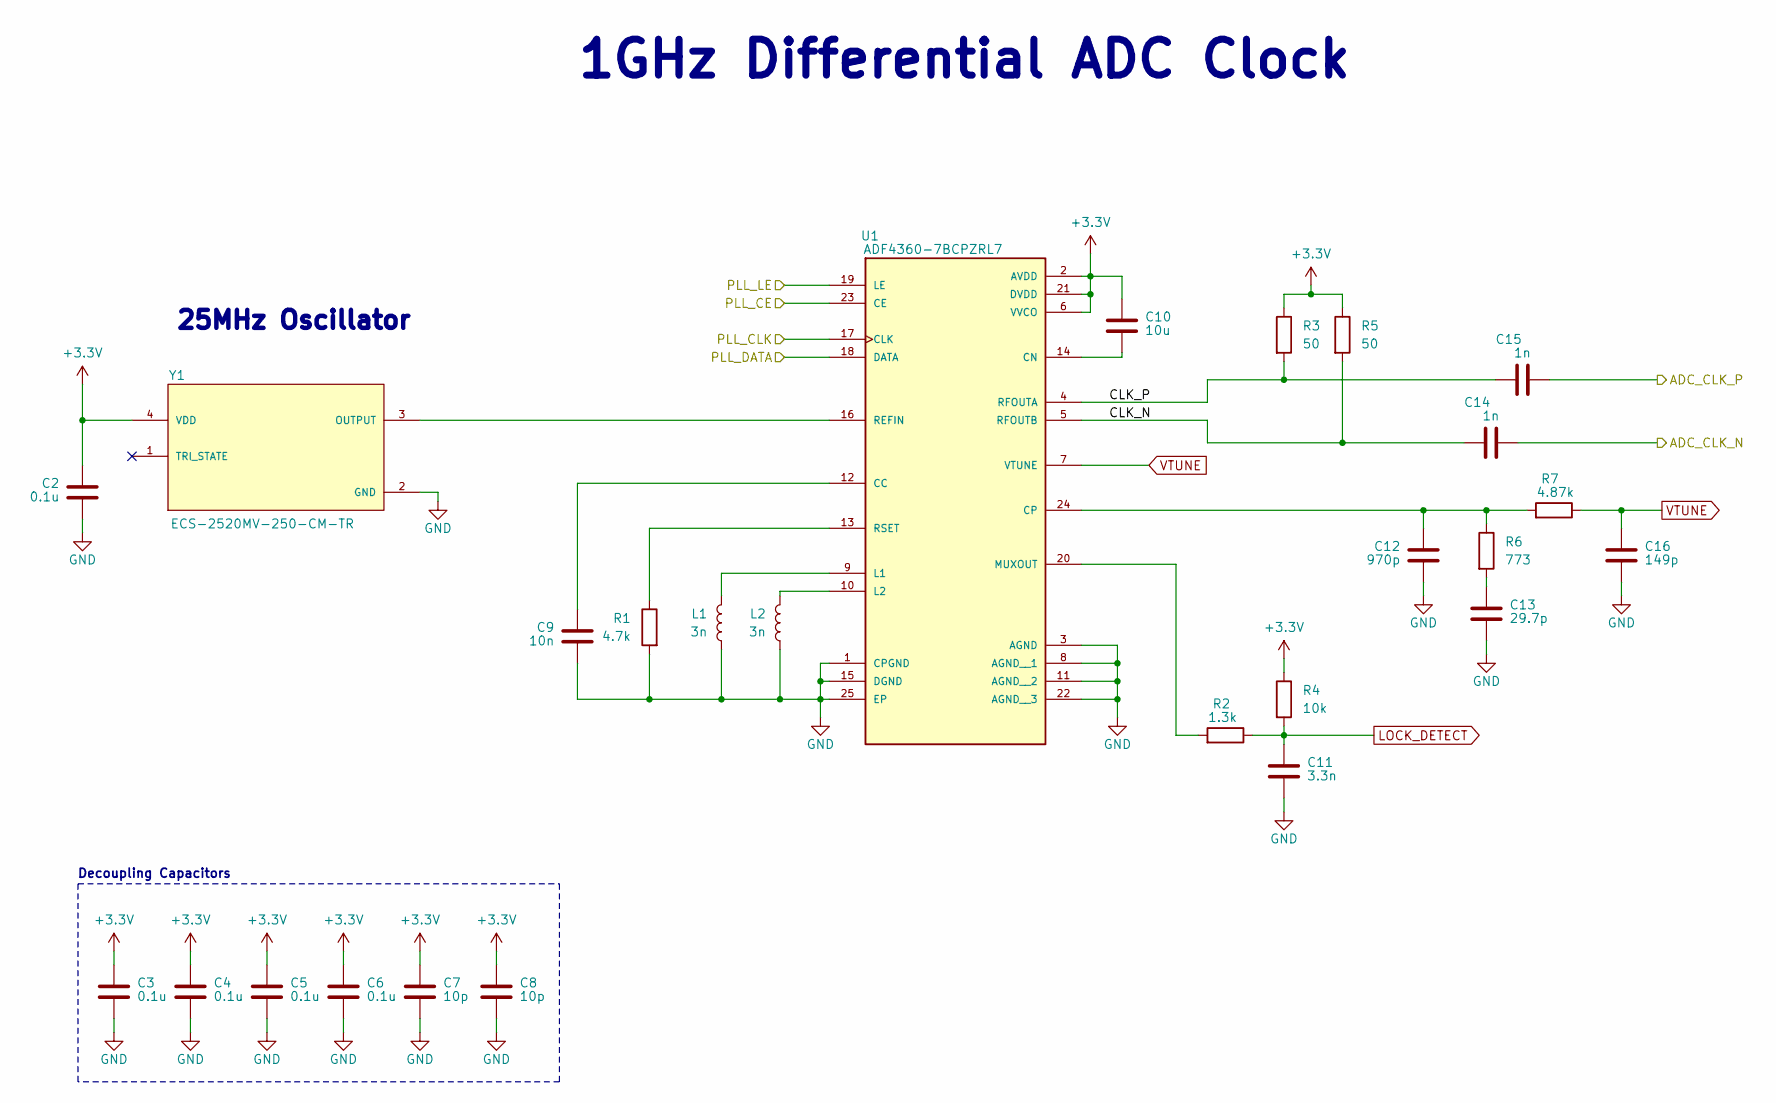
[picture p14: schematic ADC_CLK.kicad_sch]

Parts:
C2, C3, C4, C5, C6: 0.1u; C_0603_1608Metric_Pad1.08x0.95mm_HandSolder
C7, C8: 10p; C_0603_1608Metric_Pad1.08x0.95mm_HandSolder
C9: 10n; C_0603_1608Metric_Pad1.08x0.95mm_HandSolder
C10: 10u; C_0603_1608Metric_Pad1.08x0.95mm_HandSolder
C11: 3.3n; C_0603_1608Metric_Pad1.08x0.95mm_HandSolder
C12: 970p; C_0603_1608Metric_Pad1.08x0.95mm_HandSolder
C13: 29.7p; C_0603_1608Metric_Pad1.08x0.95mm_HandSolder
C14, C15: 1n; C_0603_1608Metric_Pad1.08x0.95mm_HandSolder
C16: 149p; C_0603_1608Metric_Pad1.08x0.95mm_HandSolder
L1, L2: 3n; INDC1006X60N
R1: 4.7k; R_0603_1608Metric_Pad0.98x0.95mm_HandSolder
R2: 1.3k; R_0603_1608Metric_Pad0.98x0.95mm_HandSolder
R3, R5: 50; R_0603_1608Metric_Pad0.98x0.95mm_HandSolder
R4: 10k; R_0603_1608Metric_Pad0.98x0.95mm_HandSolder
R6: 773; R_0603_1608Metric_Pad0.98x0.95mm_HandSolder
R7: 4.87k; R_0603_1608Metric_Pad0.98x0.95mm_HandSolder
U1: ADF4360-7BCPZRL7; QFN50P400X400X80-25N; PARTREV F
Y1: ECS-2520MV-250-CM-TR; Oscillator_SMD_ECS_2520MV-xxx-xx-4Pin_2.5x2.0mm

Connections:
+3.3V: C2.1, C3.1, C4.1, C5.1, C6.1, C7.1, C8.1, C10.1, R3.1, R4.1, R5.1, U1.2 (AVDD), U1.6 (VVCO), U1.21 (DVDD), Y1.4 (VDD); also elsewhere on the board
/ADC Clock/ADC_CLK_N: C14.1; also elsewhere on the board
/ADC Clock/ADC_CLK_P: C15.1; also elsewhere on the board
/ADC Clock/CLK_N: C14.2, R5.2, U1.5 (RFOUTB)
/ADC Clock/CLK_P: C15.2, R3.2, U1.4 (RFOUTA)
/ADC Clock/PLL_CE: U1.23 (CE); also elsewhere on the board
/ADC Clock/PLL_CLK: U1.17 (CLK); also elsewhere on the board
/ADC Clock/PLL_DATA: U1.18 (DATA); also elsewhere on the board
/ADC Clock/PLL_LE: U1.19 (LE); also elsewhere on the board
GND: C2.2, C3.2, C4.2, C5.2, C6.2, C7.2, C8.2, C9.2, C11.2, C12.2, C13.2, C16.2, L1.2, L2.2, R1.2, U1.1 (CPGND), U1.3 (AGND), U1.8 (AGND__1), U1.11 (AGND__2), U1.15 (DGND), U1.22 (AGND__3), U1.25 (EP), Y1.2 (GND); also elsewhere on the board
LOCK_DETECT: C11.1, R2.1, R4.2
unnamed: C13.1, R6.2
unnamed: C9.1, U1.12 (CC)
unnamed: C10.2, U1.14 (CN)
unnamed: C12.1, R6.1, R7.2, U1.24 (CP)
unnamed: L1.1, U1.9 (L1)
unnamed: L2.1, U1.10 (L2)
unnamed: R2.2, U1.20 (MUXOUT)
unnamed: U1.16 (REFIN), Y1.3 (OUTPUT)
unnamed: R1.1, U1.13 (RSET)
VTUNE: C16.1, R7.1, U1.7 (VTUNE)

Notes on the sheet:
Decoupling Capacitors
1GHz Differential ADC Clock
25MHz Oscillator

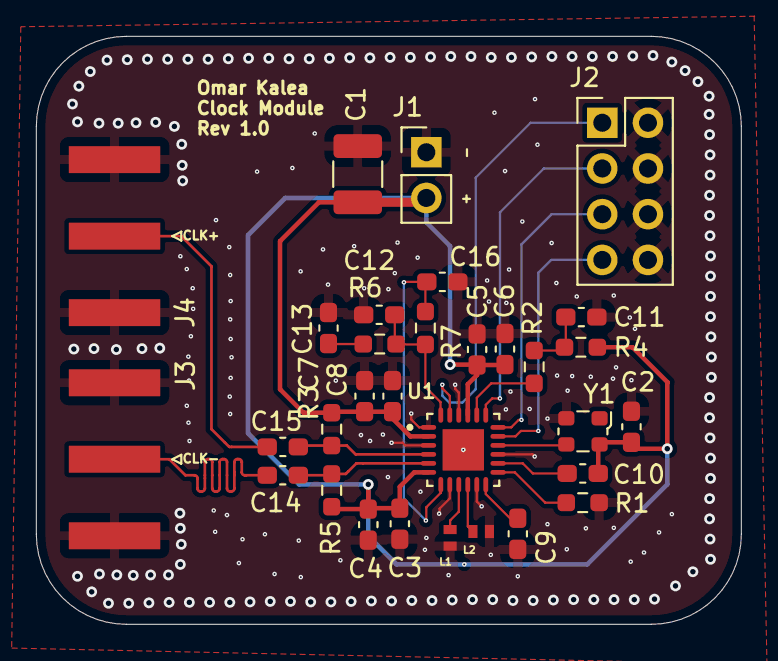
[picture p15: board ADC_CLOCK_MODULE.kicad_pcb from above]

Board: 4 copper layers, 39.2 x 32.7 mm, 31 parts (0 on the bottom side), 21 nets.

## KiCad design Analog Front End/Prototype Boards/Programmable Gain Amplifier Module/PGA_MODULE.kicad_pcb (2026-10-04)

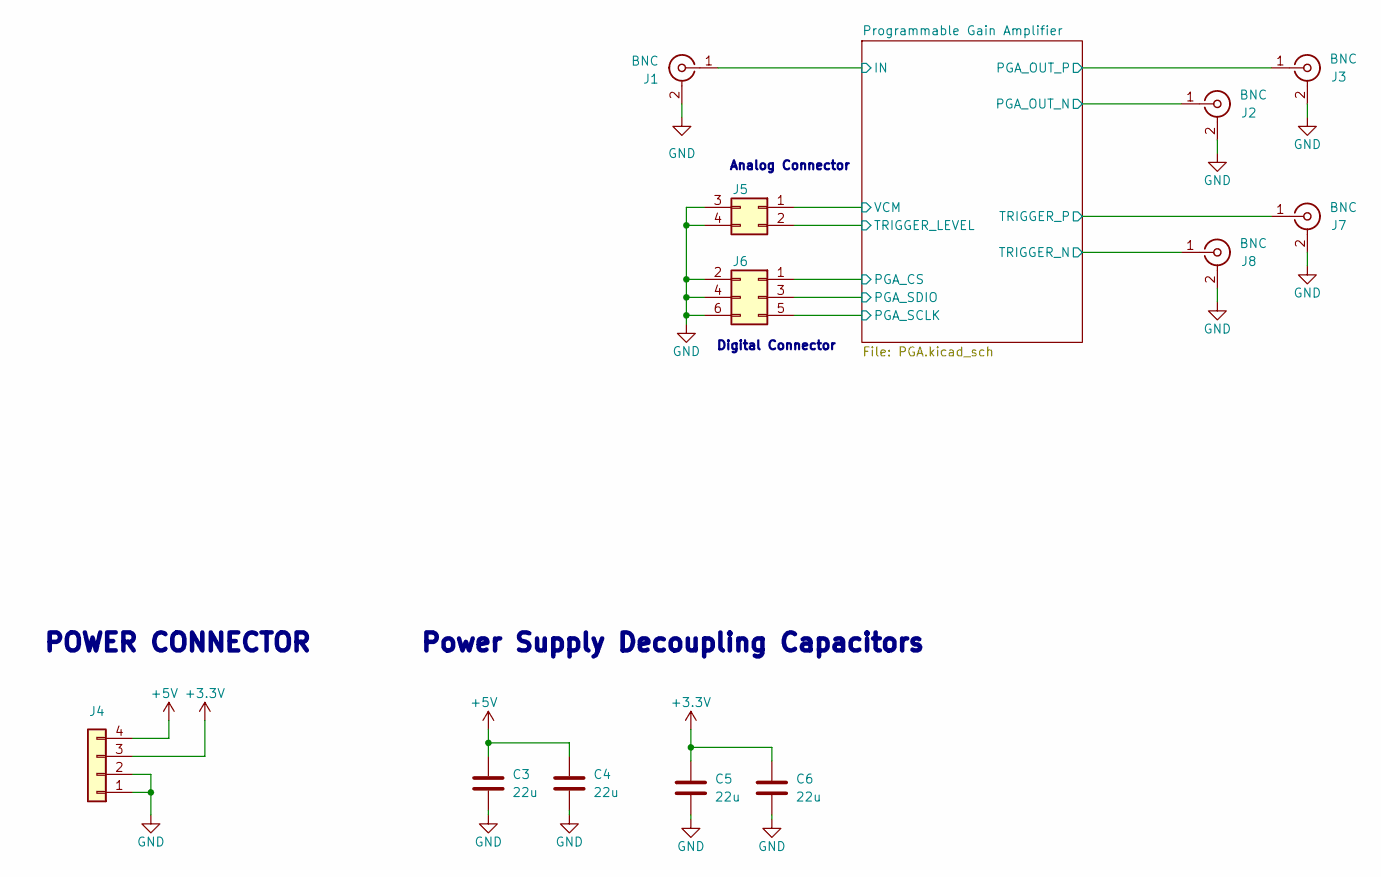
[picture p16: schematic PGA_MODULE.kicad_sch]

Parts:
C3, C4, C5, C6: 22u; C_1210_3225Metric_Pad1.33x2.70mm_HandSolder
J1, J2, J3, J7, J8: BNC; CONN_73100-0105_MOL
J4: Conn_01x04; PinHeader_2x02_P2.54mm_Vertical
J5: Conn_02x02_Top_Bottom; PinHeader_2x02_P2.54mm_Vertical
J6: Conn_02x03_Odd_Even; PinSocket_2x03_P2.54mm_Vertical

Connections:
+3.3V: C5.1, C6.1, J4.3; also elsewhere on the board
+5V: C3.1, C4.1, J4.4; also elsewhere on the board
/Programmable Gain Amplifier/IN: J1.1 (In); also elsewhere on the board
/Programmable Gain Amplifier/PGA_CS: J6.1; also elsewhere on the board
/Programmable Gain Amplifier/PGA_OUT_N: J2.1 (In); also elsewhere on the board
/Programmable Gain Amplifier/PGA_OUT_P: J3.1 (In); also elsewhere on the board
/Programmable Gain Amplifier/PGA_SCLK: J6.5; also elsewhere on the board
/Programmable Gain Amplifier/PGA_SDIO: J6.3; also elsewhere on the board
/Programmable Gain Amplifier/TRIGGER_LEVEL: J5.2; also elsewhere on the board
/Programmable Gain Amplifier/TRIGGER_N: J8.1 (In); also elsewhere on the board
/Programmable Gain Amplifier/TRIGGER_P: J7.1 (In); also elsewhere on the board
/Programmable Gain Amplifier/VCM: J5.1; also elsewhere on the board
GND: C3.2, C4.2, C5.2, C6.2, J1.2 (Ext), J1.3, J2.2 (Ext), J2.3, J3.2 (Ext), J3.3, J4.1, J4.2, J5.3, J5.4, J6.2, J6.4, J6.6, J7.2 (Ext), J7.3, J8.2 (Ext), J8.3; also elsewhere on the board

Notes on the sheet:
Analog Connector
Digital Connector
POWER CONNECTOR
Power Supply Decoupling Capacitors

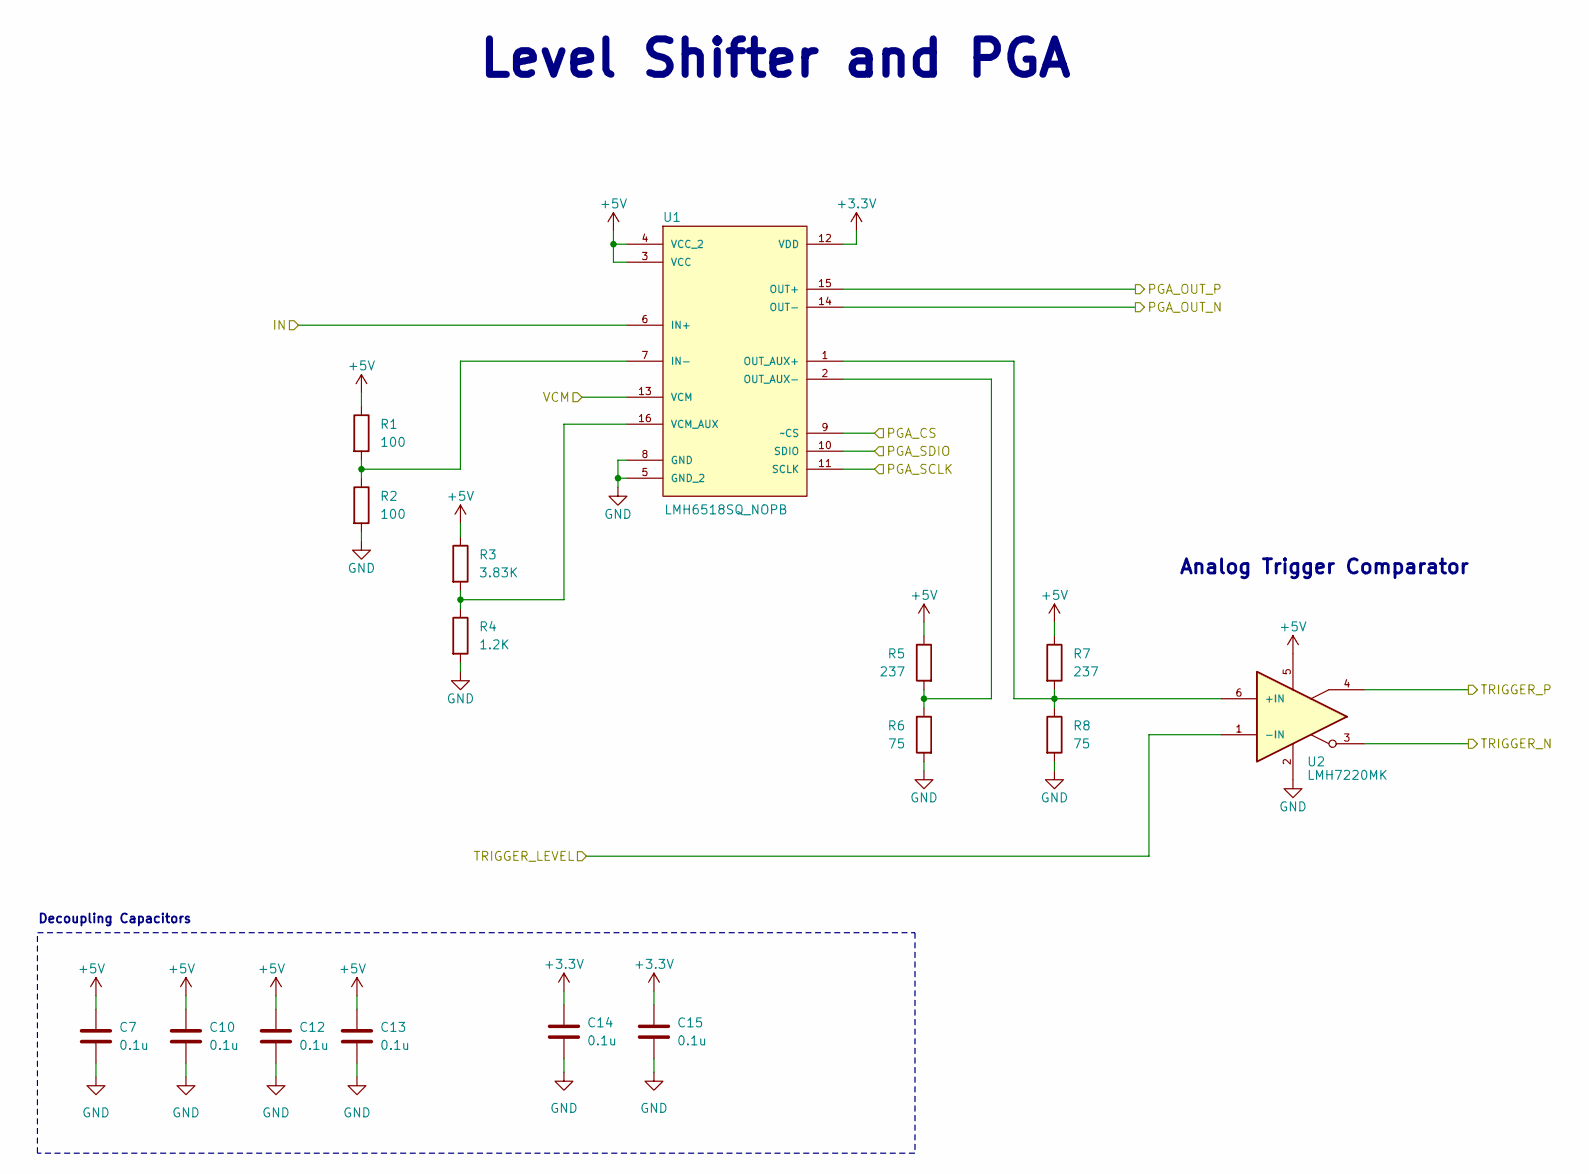
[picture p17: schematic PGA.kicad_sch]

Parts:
C7, C10, C12, C13, C14, C15: 0.1u; C_0603_1608Metric
R1, R2: 100; R_0603_1608Metric_Pad0.98x0.95mm_HandSolder
R3: 3.83K; R_0603_1608Metric_Pad0.98x0.95mm_HandSolder
R4: 1.2K; R_0603_1608Metric_Pad0.98x0.95mm_HandSolder
R5, R7: 237; R_0603_1608Metric_Pad0.98x0.95mm_HandSolder
R6, R8: 75; R_0603_1608Metric_Pad0.98x0.95mm_HandSolder
U1: LMH6518SQ_NOPB; QFN50P400X400X80-17N; MPN LMH6518SQ/NOPB
U2: LMH7220MK; SOT95P280X110-6N

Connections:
+3.3V: C14.1, C15.1, U1.12 (VDD); also elsewhere on the board
+5V: C7.1, C10.1, C12.1, C13.1, R1.1, R3.1, R5.1, R7.1, U1.3 (VCC), U1.4 (VCC_2), U2.5; also elsewhere on the board
/Programmable Gain Amplifier/IN: U1.6 (IN+); also elsewhere on the board
/Programmable Gain Amplifier/PGA_CS: U1.9 (~CS); also elsewhere on the board
/Programmable Gain Amplifier/PGA_OUT_N: U1.14 (OUT-); also elsewhere on the board
/Programmable Gain Amplifier/PGA_OUT_P: U1.15 (OUT+); also elsewhere on the board
/Programmable Gain Amplifier/PGA_SCLK: U1.11 (SCLK); also elsewhere on the board
/Programmable Gain Amplifier/PGA_SDIO: U1.10 (SDIO); also elsewhere on the board
/Programmable Gain Amplifier/TRIGGER_LEVEL: U2.1 (-IN); also elsewhere on the board
/Programmable Gain Amplifier/TRIGGER_N: U2.3; also elsewhere on the board
/Programmable Gain Amplifier/TRIGGER_P: U2.4; also elsewhere on the board
/Programmable Gain Amplifier/VCM: U1.13 (VCM); also elsewhere on the board
GND: C7.2, C10.2, C12.2, C13.2, C14.2, C15.2, R2.2, R4.2, R6.2, R8.2, U1.5 (GND_2), U1.8 (GND), U1.17, U2.2; also elsewhere on the board
unnamed: R1.2, R2.1, U1.7 (IN-)
unnamed: R7.2, R8.1, U1.1 (OUT_AUX+), U2.6 (+IN)
unnamed: R5.2, R6.1, U1.2 (OUT_AUX-)
unnamed: R3.2, R4.1, U1.16 (VCM_AUX)

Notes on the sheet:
Decoupling Capacitors
Analog Trigger Comparator
Level Shifter and PGA

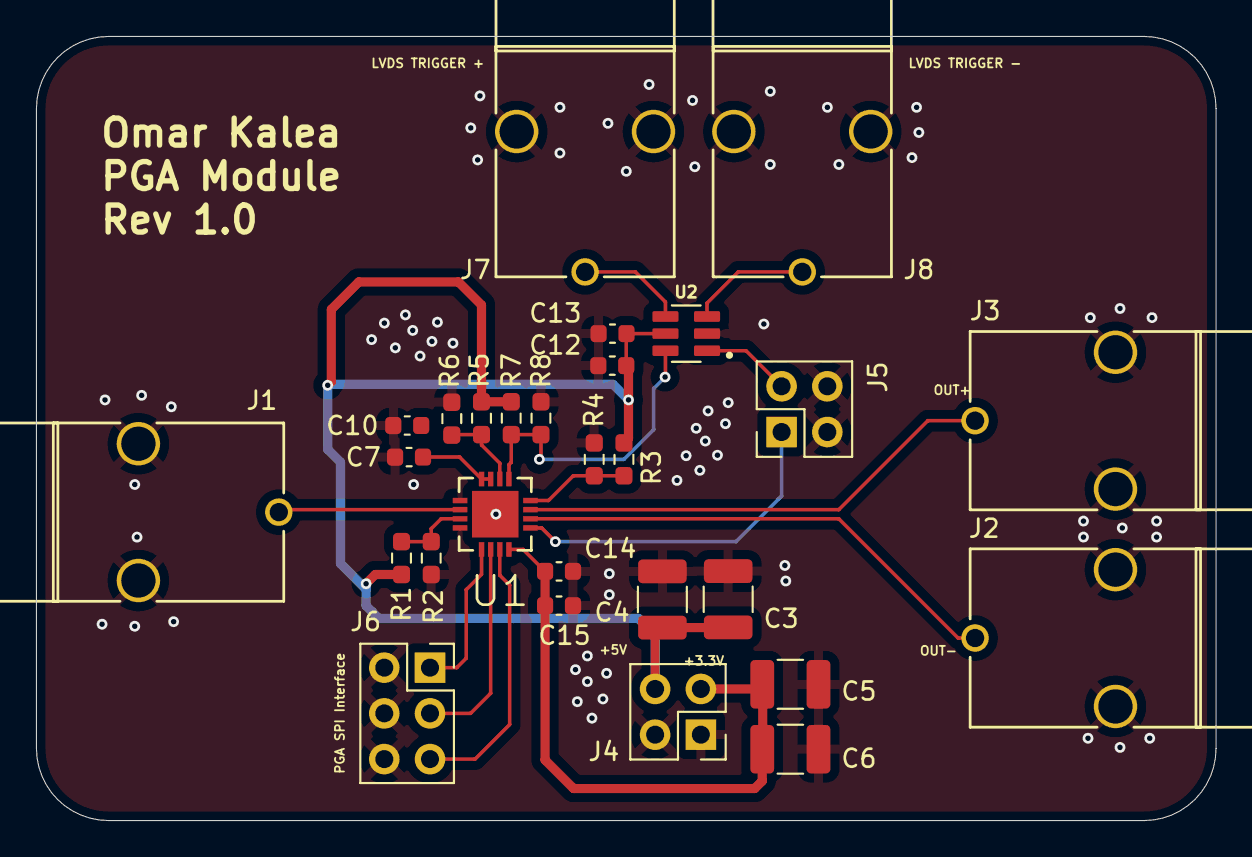
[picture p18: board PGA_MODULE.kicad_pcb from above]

Board: 4 copper layers, 65.5 x 43.6 mm, 28 parts (0 on the bottom side), 17 nets.

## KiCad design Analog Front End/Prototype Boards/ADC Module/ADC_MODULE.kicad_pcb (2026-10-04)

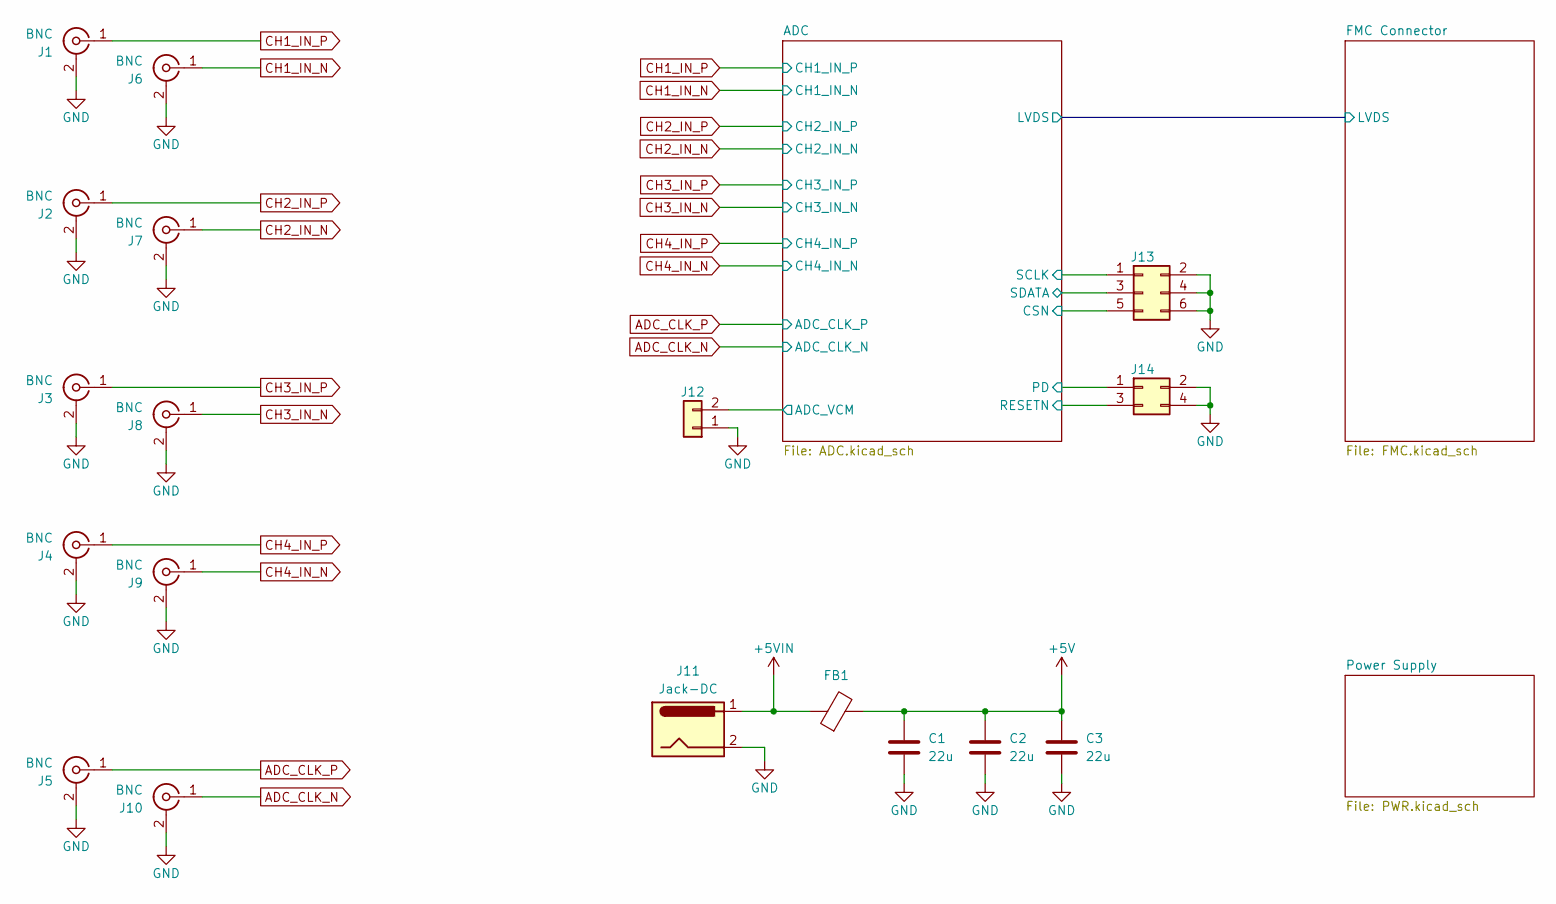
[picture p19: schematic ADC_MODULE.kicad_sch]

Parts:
C1, C2, C3: 22u; C_1210_3225Metric_Pad1.33x2.70mm_HandSolder
FB1: FerriteBead; BEADC1005X55N
J1, J2, J3, J4, J6, J7, J8, J9: BNC; SMA_Amphenol_132289_EdgeMount
J5, J10: BNC; SMA_Amphenol_132134_Vertical
J11: Jack-DC; BarrelJack_Kycon_KLDX-0202-xC_Horizontal
J12: Conn_01x02; PinHeader_1x02_P2.54mm_Vertical
J13: Conn_02x03_Odd_Even; PinHeader_2x03_P2.54mm_Vertical
J14: Conn_02x02_Odd_Even; PinHeader_2x02_P2.54mm_Vertical

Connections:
+5V: C1.1, C2.1, C3.1, FB1.2; also elsewhere on the board
+5VIN: FB1.1, J11.1
/ADC/ADC_VCM: J12.2; also elsewhere on the board
/ADC/CSN: J13.5; also elsewhere on the board
/ADC/PD: J14.1; also elsewhere on the board
/ADC/RESETN: J14.3; also elsewhere on the board
/ADC/SCLK: J13.1; also elsewhere on the board
/ADC/SDATA: J13.3; also elsewhere on the board
ADC_CLK_N: J10.1 (In); also elsewhere on the board
ADC_CLK_P: J5.1 (In); also elsewhere on the board
CH1_IN_N: J6.1 (In); also elsewhere on the board
CH1_IN_P: J1.1 (In); also elsewhere on the board
CH2_IN_N: J7.1 (In); also elsewhere on the board
CH2_IN_P: J2.1 (In); also elsewhere on the board
CH3_IN_N: J8.1 (In); also elsewhere on the board
CH3_IN_P: J3.1 (In); also elsewhere on the board
CH4_IN_N: J9.1 (In); also elsewhere on the board
CH4_IN_P: J4.1 (In); also elsewhere on the board
GND: C1.2, C2.2, C3.2, J1.2 (Ext), J2.2 (Ext), J3.2 (Ext), J4.2 (Ext), J5.2 (Ext), J6.2 (Ext), J7.2 (Ext), J8.2 (Ext), J9.2 (Ext), J10.2 (Ext), J11.2, J11.3, J12.1, J13.2, J13.4, J13.6, J14.2, J14.4; also elsewhere on the board

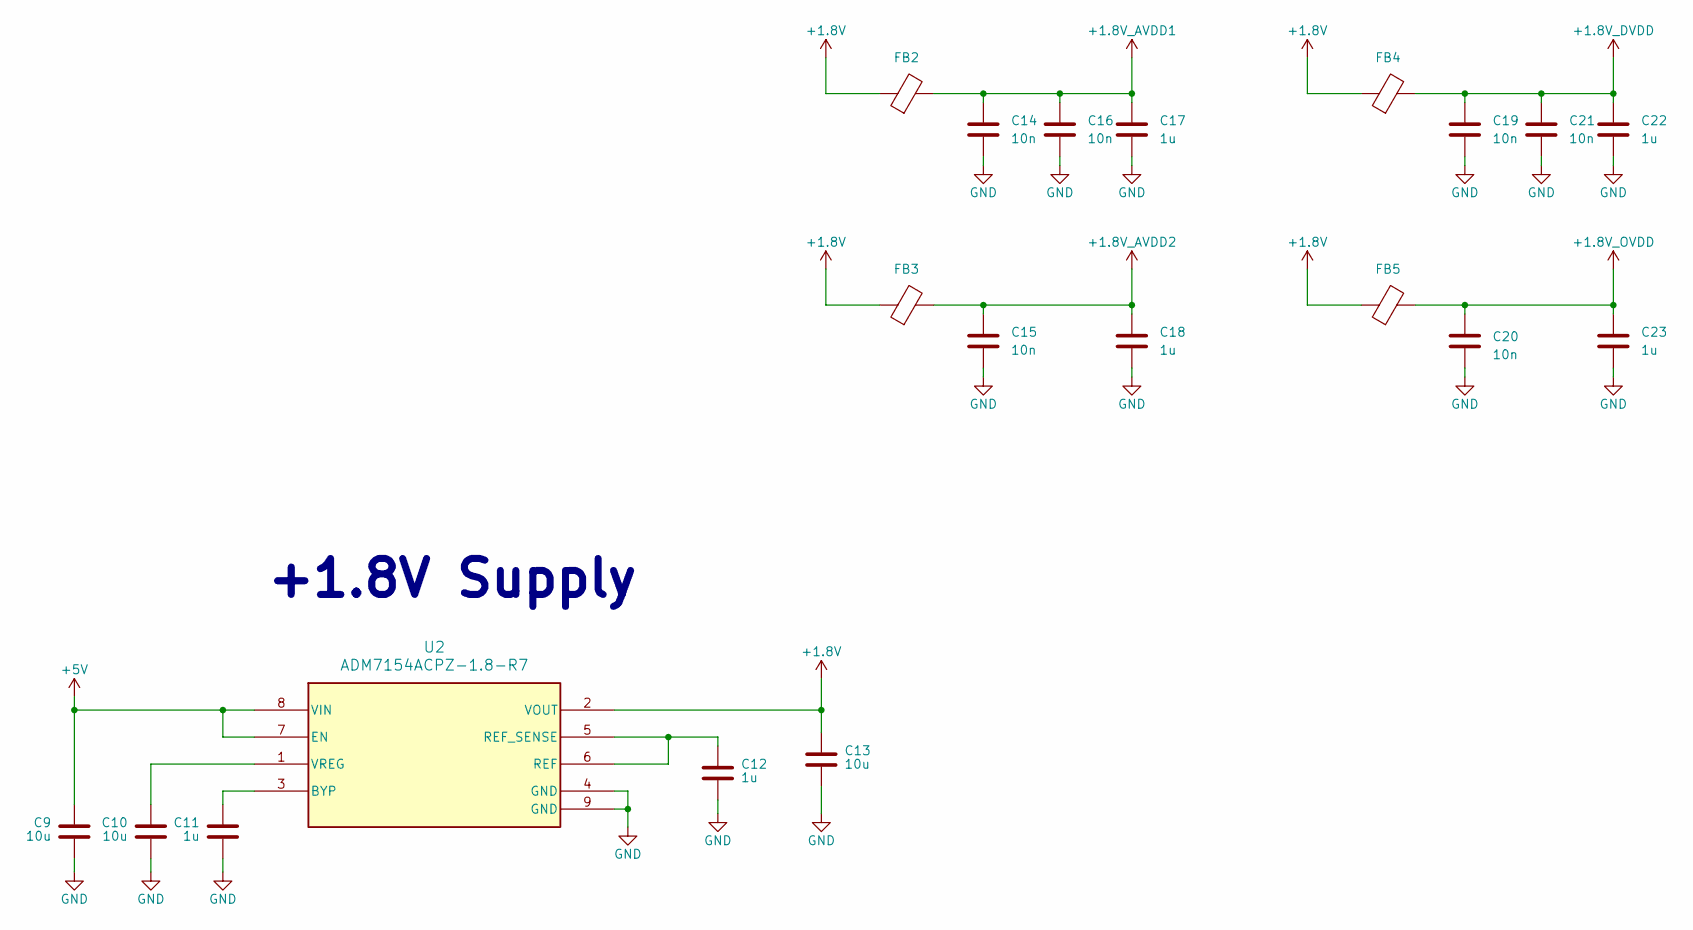
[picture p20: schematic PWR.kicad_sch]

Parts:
C9, C10, C13: 10u; C_0603_1608Metric_Pad1.08x0.95mm_HandSolder
C11, C12, C17, C18, C22, C23: 1u; C_0603_1608Metric_Pad1.08x0.95mm_HandSolder
C14, C15, C16, C19, C20, C21: 10n; C_0603_1608Metric_Pad1.08x0.95mm_HandSolder
FB2, FB3, FB4, FB5: FerriteBead; BEADC1005X55N
U2: ADM7154ACPZ-1.8-R7; ADM7154ARDZ_1_8_R7

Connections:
+1.8V: C13.1, FB2.1, FB3.1, FB4.1, FB5.1, U2.2 (VOUT)
+1.8V_AVDD1: C14.2, C16.2, C17.2, FB2.2; also elsewhere on the board
+1.8V_AVDD2: C15.2, C18.2, FB3.2; also elsewhere on the board
+1.8V_DVDD: C19.2, C21.2, C22.2, FB4.2; also elsewhere on the board
+1.8V_OVDD: C20.2, C23.2, FB5.2; also elsewhere on the board
+5V: C9.1, U2.7 (EN), U2.8 (VIN); also elsewhere on the board
GND: C9.2, C10.2, C11.2, C12.2, C13.2, C14.1, C15.1, C16.1, C17.1, C18.1, C19.1, C20.1, C21.1, C22.1, C23.1, U2.4 (GND), U2.9 (GND); also elsewhere on the board
unnamed: C11.1, U2.3 (BYP)
unnamed: C12.1, U2.5 (REF_SENSE), U2.6 (REF)
unnamed: C10.1, U2.1 (VREG)

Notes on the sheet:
+1.8V Supply

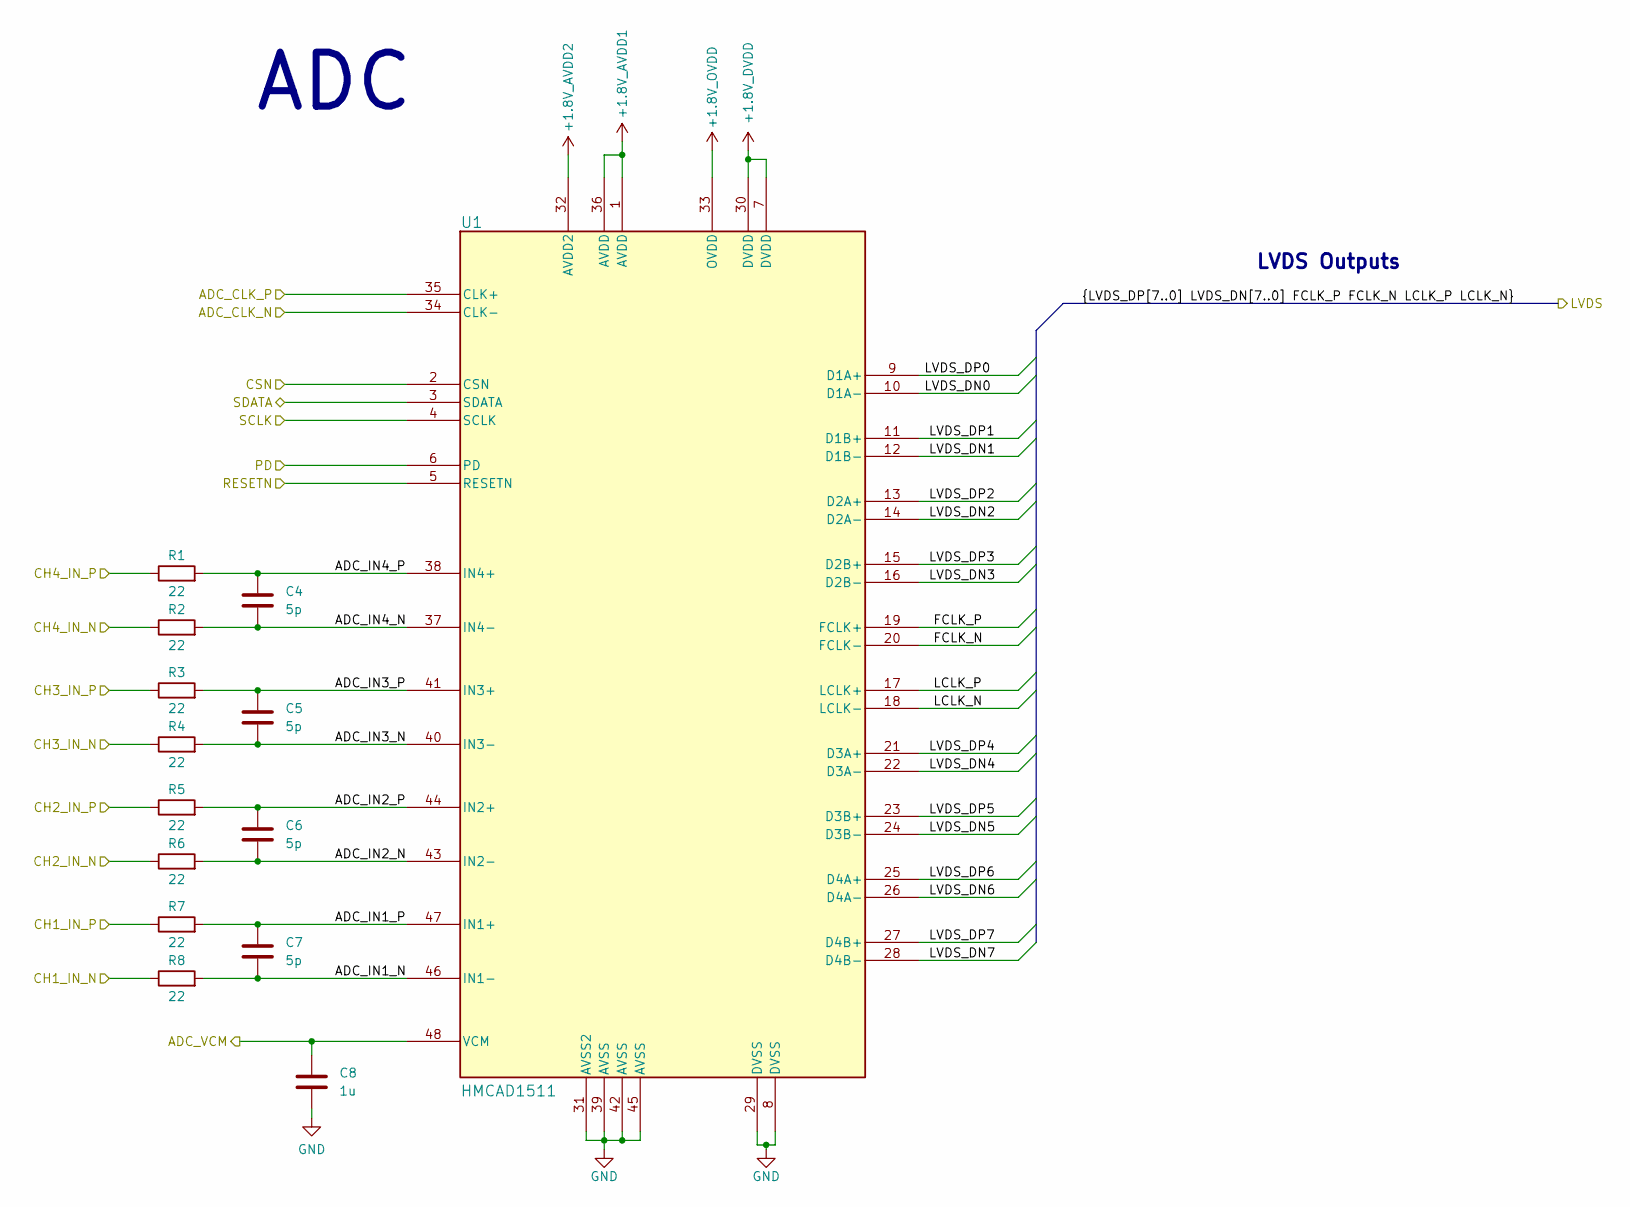
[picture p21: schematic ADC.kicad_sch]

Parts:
C4, C5, C6, C7: 5p; C_0603_1608Metric_Pad1.08x0.95mm_HandSolder
C8: 1u; C_0603_1608Metric_Pad1.08x0.95mm_HandSolder
R1, R2, R3, R4, R5, R6, R7, R8: 22; R_0603_1608Metric_Pad0.98x0.95mm_HandSolder
U1: HMCAD1511; CP-48-22_ADI-L

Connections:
+1.8V_AVDD1: U1.1 (AVDD), U1.36 (AVDD); also elsewhere on the board
+1.8V_AVDD2: U1.32 (AVDD2); also elsewhere on the board
+1.8V_DVDD: U1.7 (DVDD), U1.30 (DVDD); also elsewhere on the board
+1.8V_OVDD: U1.33 (OVDD); also elsewhere on the board
/ADC/ADC_IN1_N: C7.1, R8.2, U1.46 (IN1-)
/ADC/ADC_IN1_P: C7.2, R7.2, U1.47 (IN1+)
/ADC/ADC_IN2_N: C6.1, R6.2, U1.43 (IN2-)
/ADC/ADC_IN2_P: C6.2, R5.2, U1.44 (IN2+)
/ADC/ADC_IN3_N: C5.1, R4.2, U1.40 (IN3-)
/ADC/ADC_IN3_P: C5.2, R3.2, U1.41 (IN3+)
/ADC/ADC_IN4_N: C4.1, R2.2, U1.37 (IN4-)
/ADC/ADC_IN4_P: C4.2, R1.2, U1.38 (IN4+)
/ADC/ADC_VCM: C8.2, U1.48 (VCM); also elsewhere on the board
/ADC/CSN: U1.2 (CSN); also elsewhere on the board
/ADC/FCLK_N: U1.20 (FCLK-); also elsewhere on the board
/ADC/FCLK_P: U1.19 (FCLK+); also elsewhere on the board
/ADC/LCLK_N: U1.18 (LCLK-); also elsewhere on the board
/ADC/LCLK_P: U1.17 (LCLK+); also elsewhere on the board
/ADC/LVDS_DN0: U1.10 (D1A-); also elsewhere on the board
/ADC/LVDS_DN1: U1.12 (D1B-); also elsewhere on the board
/ADC/LVDS_DN2: U1.14 (D2A-); also elsewhere on the board
/ADC/LVDS_DN3: U1.16 (D2B-); also elsewhere on the board
/ADC/LVDS_DN4: U1.22 (D3A-); also elsewhere on the board
/ADC/LVDS_DN5: U1.24 (D3B-); also elsewhere on the board
/ADC/LVDS_DN6: U1.26 (D4A-); also elsewhere on the board
/ADC/LVDS_DN7: U1.28 (D4B-); also elsewhere on the board
/ADC/LVDS_DP0: U1.9 (D1A+); also elsewhere on the board
/ADC/LVDS_DP1: U1.11 (D1B+); also elsewhere on the board
/ADC/LVDS_DP2: U1.13 (D2A+); also elsewhere on the board
/ADC/LVDS_DP3: U1.15 (D2B+); also elsewhere on the board
/ADC/LVDS_DP4: U1.21 (D3A+); also elsewhere on the board
/ADC/LVDS_DP5: U1.23 (D3B+); also elsewhere on the board
/ADC/LVDS_DP6: U1.25 (D4A+); also elsewhere on the board
/ADC/LVDS_DP7: U1.27 (D4B+); also elsewhere on the board
/ADC/PD: U1.6 (PD); also elsewhere on the board
/ADC/RESETN: U1.5 (RESETN); also elsewhere on the board
/ADC/SCLK: U1.4 (SCLK); also elsewhere on the board
/ADC/SDATA: U1.3 (SDATA); also elsewhere on the board
ADC_CLK_N: U1.34 (CLK-); also elsewhere on the board
ADC_CLK_P: U1.35 (CLK+); also elsewhere on the board
CH1_IN_N: R8.1; also elsewhere on the board
CH1_IN_P: R7.1; also elsewhere on the board
CH2_IN_N: R6.1; also elsewhere on the board
CH2_IN_P: R5.1; also elsewhere on the board
CH3_IN_N: R4.1; also elsewhere on the board
CH3_IN_P: R3.1; also elsewhere on the board
CH4_IN_N: R2.1; also elsewhere on the board
CH4_IN_P: R1.1; also elsewhere on the board
GND: C8.1, U1.8 (DVSS), U1.29 (DVSS), U1.31 (AVSS2), U1.39 (AVSS), U1.42 (AVSS), U1.45 (AVSS), U1.49; also elsewhere on the board

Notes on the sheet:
ADC
LVDS Outputs

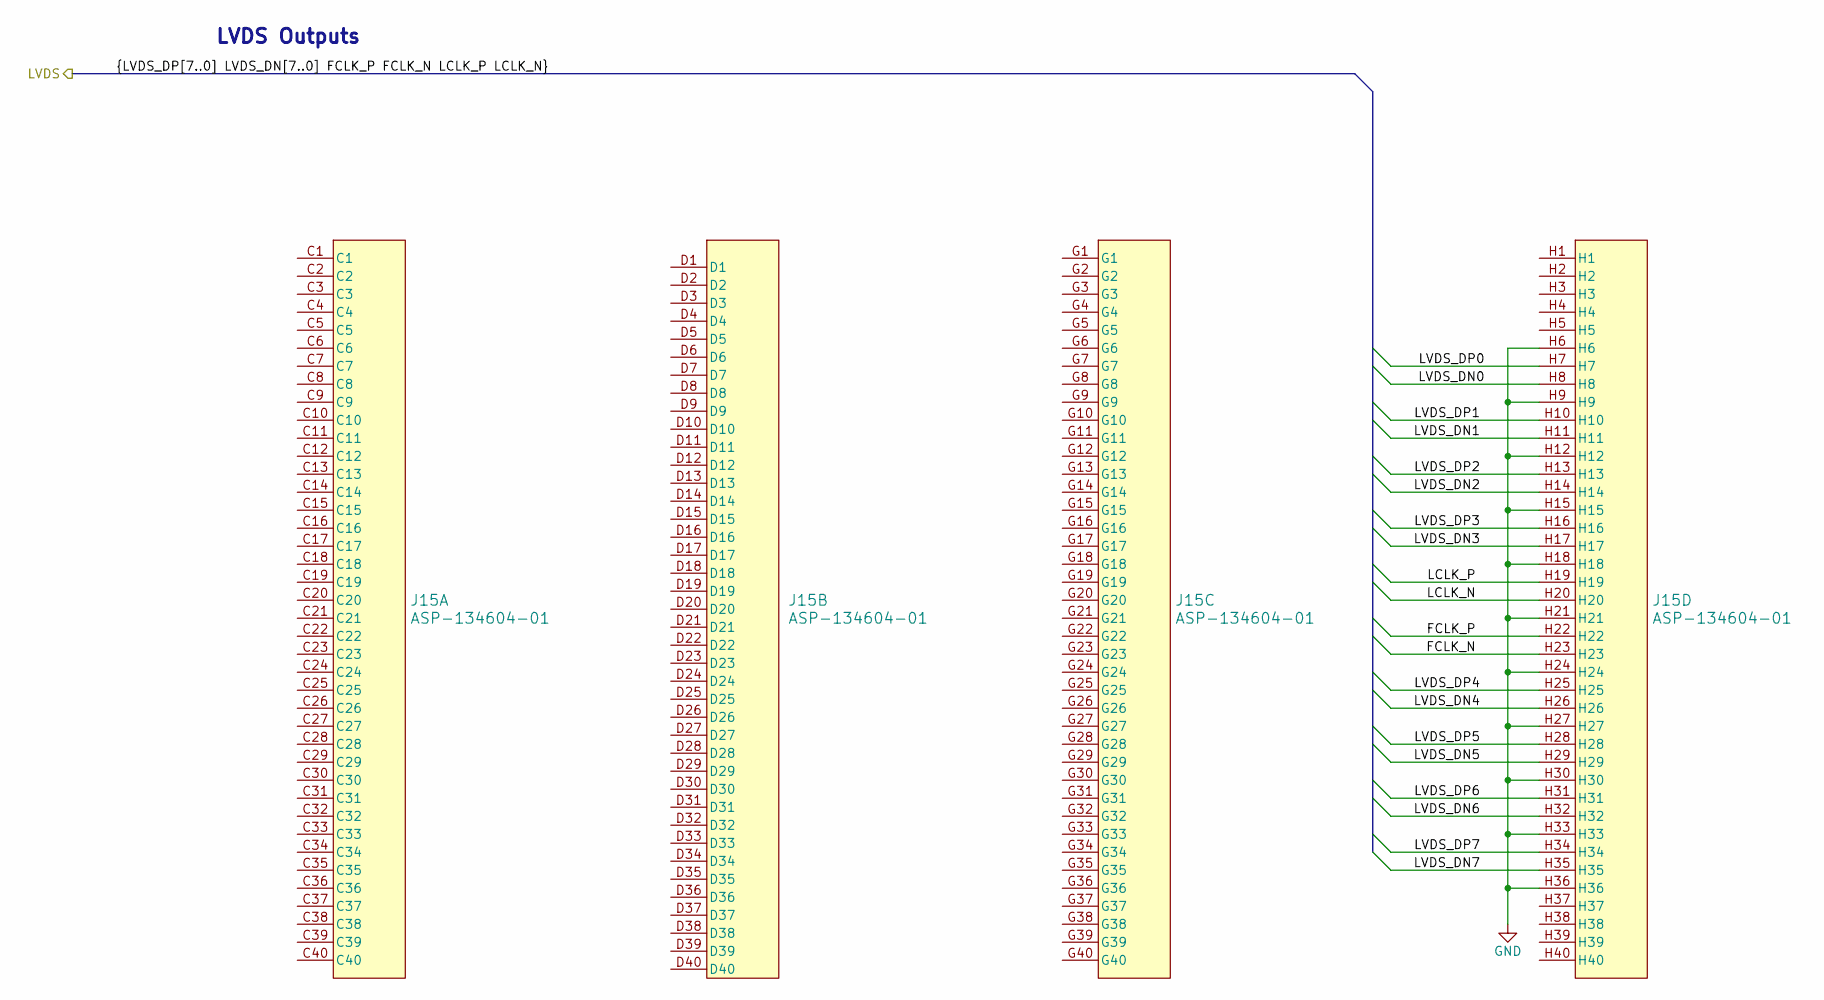
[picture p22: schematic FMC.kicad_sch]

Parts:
J15: ASP-134604-01; SAMTEC_ASP-134604-01

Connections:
/ADC/FCLK_N: J15.H23; also elsewhere on the board
/ADC/FCLK_P: J15.H22; also elsewhere on the board
/ADC/LCLK_N: J15.H20; also elsewhere on the board
/ADC/LCLK_P: J15.H19; also elsewhere on the board
/ADC/LVDS_DN0: J15.H8; also elsewhere on the board
/ADC/LVDS_DN1: J15.H11; also elsewhere on the board
/ADC/LVDS_DN2: J15.H14; also elsewhere on the board
/ADC/LVDS_DN3: J15.H17; also elsewhere on the board
/ADC/LVDS_DN4: J15.H26; also elsewhere on the board
/ADC/LVDS_DN5: J15.H29; also elsewhere on the board
/ADC/LVDS_DN6: J15.H32; also elsewhere on the board
/ADC/LVDS_DN7: J15.H35; also elsewhere on the board
/ADC/LVDS_DP0: J15.H7; also elsewhere on the board
/ADC/LVDS_DP1: J15.H10; also elsewhere on the board
/ADC/LVDS_DP2: J15.H13; also elsewhere on the board
/ADC/LVDS_DP3: J15.H16; also elsewhere on the board
/ADC/LVDS_DP4: J15.H25; also elsewhere on the board
/ADC/LVDS_DP5: J15.H28; also elsewhere on the board
/ADC/LVDS_DP6: J15.H31; also elsewhere on the board
/ADC/LVDS_DP7: J15.H34; also elsewhere on the board
GND: J15.H6, J15.H9, J15.H12, J15.H15, J15.H18, J15.H21, J15.H24, J15.H27, J15.H30, J15.H33, J15.H36; also elsewhere on the board

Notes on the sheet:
LVDS Outputs

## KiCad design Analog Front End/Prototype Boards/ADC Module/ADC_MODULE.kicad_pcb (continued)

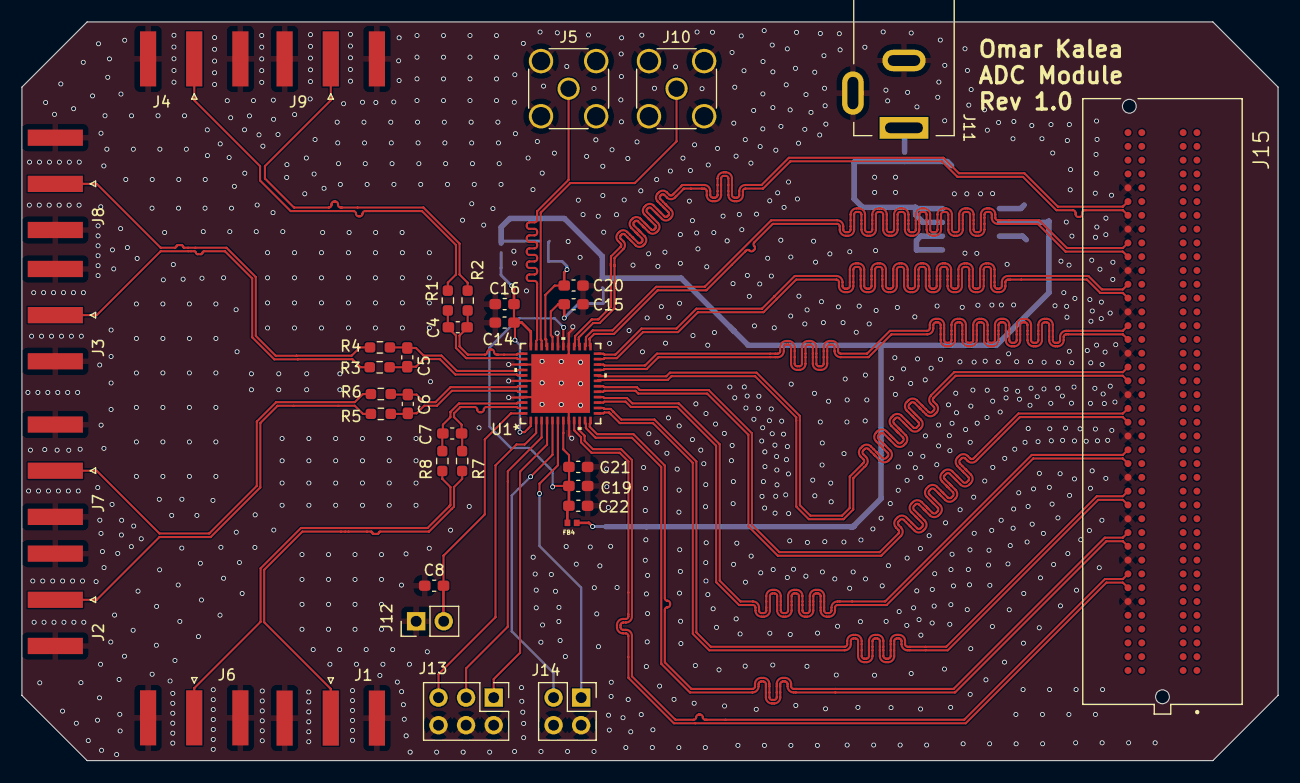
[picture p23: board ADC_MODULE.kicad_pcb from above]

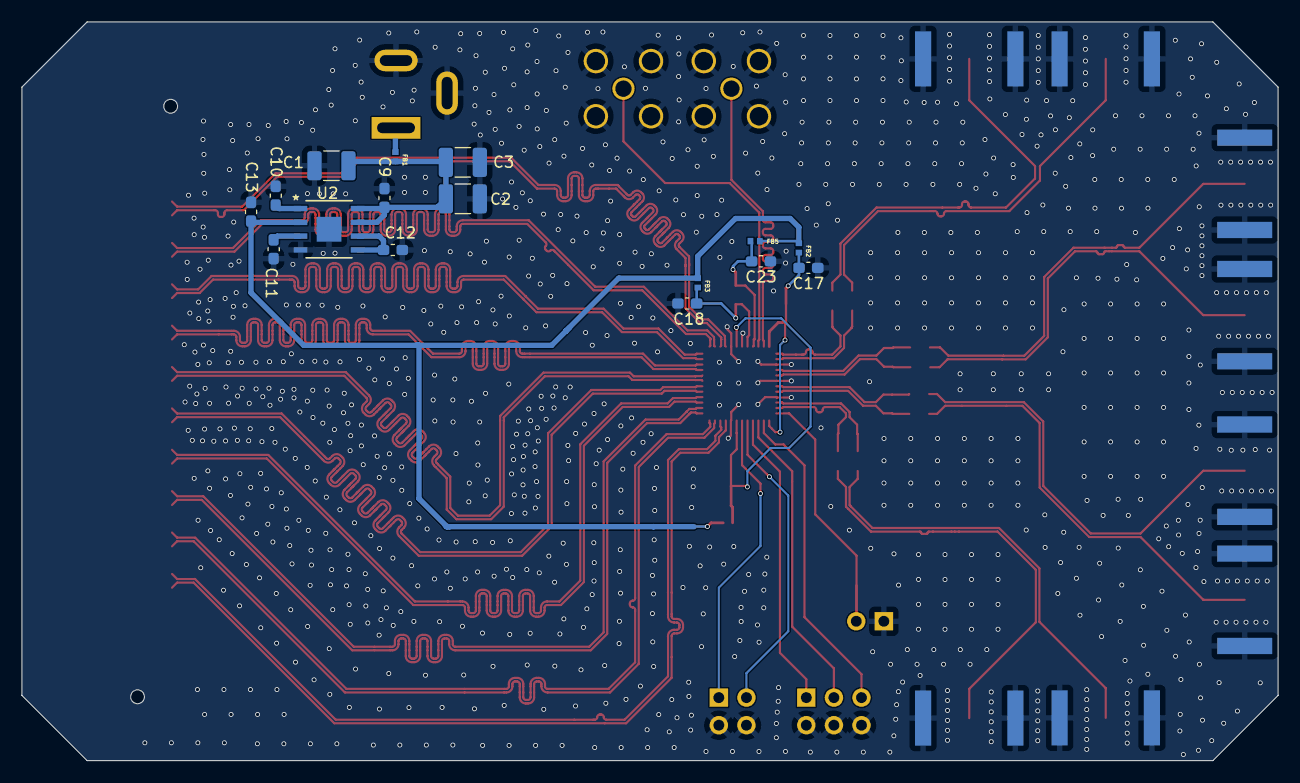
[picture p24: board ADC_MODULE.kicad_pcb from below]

Board: 4 copper layers, 115.7 x 68.0 mm, 53 parts (16 on the bottom side), 55 nets.

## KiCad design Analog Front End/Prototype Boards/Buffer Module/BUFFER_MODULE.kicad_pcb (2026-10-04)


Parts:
C1, C2: 1u; C_0603_1608Metric
C3, C4, C5, C6: 22u; C_1210_3225Metric_Pad1.33x2.70mm_HandSolder
D1, D2: BZX84C3V3LT1G; SOT95P240X111-3N; PARTREV 23
J1, J2: BNC; CONN_73100-0105_MOL
J3: Conn_01x04; PinHeader_2x02_P2.54mm_Vertical
J4, J5: Conn_02x03_Counter_Clockwise; PinHeader_2x03_P2.54mm_Vertical
J6: Conn_02x02_Top_Bottom; PinHeader_2x02_P2.54mm_Vertical
R1, R2: 1k; R_0603_1608Metric

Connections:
+1.7V_CLL: C1.2, D1.3, J5.5, R1.2
+3.3V_CLH: C2.2, D2.1, J4.1, R2.1
+5V: C3.1, C4.1, D2.3, J3.4, R1.1; also elsewhere on the board
-5V: C5.1, C6.1, J3.3; also elsewhere on the board
/DC Offset Control/DC_OFFSET_DOWN: J6.2; also elsewhere on the board
/DC Offset Control/DC_OFFSET_UP: J6.1; also elsewhere on the board
/EXT_CLH: J4.5, J4.6
/EXT_CLL: J5.1, J5.2
/JFET Buffer/BUFF_IN: J1.1 (In); also elsewhere on the board
/JFET Buffer/BUFF_OUT: J2.1 (In); also elsewhere on the board
/JFET Buffer/CLH: J4.3; also elsewhere on the board
/JFET Buffer/CLL: J5.3; also elsewhere on the board
GND: C1.1, C2.1, C3.2, C4.2, C5.2, C6.2, D1.1, D1.2, D2.2, J1.2 (Ext), J1.3, J2.2 (Ext), J2.3, J3.1, J3.2, J4.2, J4.4, J5.4, J5.6, J6.3, J6.4, R2.2; also elsewhere on the board

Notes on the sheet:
Connect Jumper to Select between on-board and external clamp voltages
Power Supply Decoupling Capacitors
DC_OFFSET = DC_OFFSET_UP - DC_OFFSET_DOWN
POWER CONNECTOR


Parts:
R15, R16, R17, R18: 500k; R_0603_1608Metric
U2, U3: OPA2140AIDGKR; DGK8; DigiKey_Part_Number 296-46321-1-ND

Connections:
+5V: U2.8, U3.8; also elsewhere on the board
-5V: U2.4, U3.4; also elsewhere on the board
/DC Offset Control/DC_OFFSET: R18.2, U2.7; also elsewhere on the board
/DC Offset Control/DC_OFFSET_DOWN: U3.3 (+); also elsewhere on the board
/DC Offset Control/DC_OFFSET_UP: U3.5 (+); also elsewhere on the board
GND: R17.2; also elsewhere on the board
unnamed: R15.2, R17.1, U2.5 (+)
unnamed: R16.2, R18.1, U2.6 (-)
unnamed: R15.1, U3.1, U3.2 (-)
unnamed: R16.1, U3.6 (-), U3.7

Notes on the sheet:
DC OFFSET SETPOINT CONTROL


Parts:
C7, C10, C12, C13, C14, C15, C16, C17: 0.1u; C_0603_1608Metric
C8: 56p; C_0603_1608Metric
C9: 330p; C_0603_1608Metric
C11: 100p; C_0603_1608Metric
R4: 833k; R_0603_1608Metric
R5: 167k; R_0603_1608Metric
R6: 30; R_0603_1608Metric
R8: 2k; R_0603_1608Metric
R9: 17.8k; R_0603_1608Metric
R10: 10M; R_0603_1608Metric
R11, R13: 80k; R_0603_1608Metric
R12: 20k; R_0603_1608Metric
R14: 50; R_0603_1608Metric
TP1, TP2, TP3, TP4: TestPoint; TestPoint_Pad_1.5x1.5mm
U1: BUF802IRGTR; VQFN16_RGT_TEX; PARTREV C
U2: OPA2140AIDGKR; DGK8; DigiKey_Part_Number 296-46321-1-ND

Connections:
+5V: C7.1, C10.1, C12.1, C13.1, U1.1 (VS+), U1.12 (VSO+), U2.8; also elsewhere on the board
-5V: C14.1, C15.1, C16.1, C17.1, U1.5 (VS-), U1.6 (AUX_BIAS), U1.8 (VS-__1), U1.10 (VSO-), U2.4; also elsewhere on the board
/DC Offset Control/DC_OFFSET: R13.2; also elsewhere on the board
/JFET Buffer/BUFF_IN: R4.1, R6.1, TP1.1; also elsewhere on the board
/JFET Buffer/BUFF_OUT: R14.2, TP2.1; also elsewhere on the board
/JFET Buffer/CLH: U1.15 (CLH); also elsewhere on the board
/JFET Buffer/CLL: U1.14 (CLL); also elsewhere on the board
GND: C7.2, C10.2, C11.1, C12.2, C13.2, C14.2, C15.2, C16.2, C17.2, R5.2, R9.2, R12.2, TP3.1, TP4.1, U1.17 (EXP); also elsewhere on the board
unnamed: C8.2, R8.1, U2.1
unnamed: C9.1, R6.2
unnamed: C9.2, R10.1, U1.2 (IN)
unnamed: C11.2, R8.2, U1.4 (IN_AUX)
unnamed: R10.2, U1.3 (IN_BIAS)
unnamed: R11.1, R14.1, U1.11 (OUT)
unnamed: R9.1, U1.7 (R_BIAS)
unnamed: R4.2, R5.1, U2.3 (+)
unnamed: C8.1, R11.2, R12.1, R13.1, U2.2 (-)

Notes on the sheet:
JFET LNA Buffer
Decoupling Capacitors



Board: 4 copper layers, 67.1 x 42.8 mm, 48 parts (4 on the bottom side), 27 nets.

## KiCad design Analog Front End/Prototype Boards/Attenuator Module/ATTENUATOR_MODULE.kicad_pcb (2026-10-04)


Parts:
C1, C2, C3, C4: 22u; C_1210_3225Metric_Pad1.33x2.70mm_HandSolder
J1: Conn_01x04; PinHeader_2x02_P2.54mm_Vertical
J2: Conn_02x03_Odd_Even; PinHeader_2x03_P2.54mm_Vertical
J3: BNC; CONN_73100-0105_MOL
J4: SMA; SAMTEC_SMA-J-P-H-ST-EM1
R1, R2, R3: 10; R_0603_1608Metric

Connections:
+5V: C1.1, C2.1, J1.3; also elsewhere on the board
-5V: C3.1, C4.1, J1.4; also elsewhere on the board
/ATTENUATORS/ATTEN_IN: J3.1 (In); also elsewhere on the board
/ATTENUATORS/ATTEN_OUT: J4.1 (In); also elsewhere on the board
/RELAY_CTRL_0: R3.2; also elsewhere on the board
/RELAY_CTRL_1: R2.1; also elsewhere on the board
/RELAY_CTRL_2: R1.1; also elsewhere on the board
GND: C1.2, C2.2, C3.2, C4.2, J1.1, J1.2, J2.1, J2.3, J2.5, J3.2 (Ext), J3.3, J4.2 (Ext), J4.2_1, J4.2_2, J4.3_1, J4.3_2; also elsewhere on the board
unnamed: J2.2, R3.1
unnamed: J2.4, R2.2
unnamed: J2.6, R1.2

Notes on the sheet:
POWER CONNECTOR
Power Supply Decoupling Capacitors


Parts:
C5, C10, C11, C12: 0.1u; C_0603_1608Metric
C6, C7: 10p; C_0603_1608Metric
C8: 990p; C_0603_1608Metric
C9: 90p; C_0603_1608Metric
D1, D2, D3: 1N914WT; D_SOD-523
D4, D5: BAT54C; SOT-23
K1, K2, K3: G6J-2FL-Y DC5; RELAY_G6J-2FL-Y DC3_OMR
Q1, Q2, Q3: 2N7002; SOT-23
R4, R5, R6: 10; R_0603_1608Metric
R7: 990k; R_0603_1608Metric
R8: 900k; R_0603_1608Metric
R9, R13: 75; R_0603_1608Metric
R10: 120; R_0603_1608Metric
R11: 10k; R_0603_1608Metric
R12: 100k; R_0603_1608Metric
TP1, TP2, TP3, TP4: TestPoint; TestPoint_Pad_1.5x1.5mm

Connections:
+5V: C10.1, C11.1, C12.1, D4.3, K1.1, K2.1, K3.1, R4.1, R5.1, R6.1; also elsewhere on the board
-5V: D5.3; also elsewhere on the board
/ATTENUATORS/1MΩ Path: K2.2, K3.3
/ATTENUATORS/10:1 Attenuator: C7.1, C9.1, K3.5, R8.1, R12.1
/ATTENUATORS/50Ω Path: K2.4, R9.1, R10.2
/ATTENUATORS/100:1 Attenuator: C6.1, C8.1, K3.7, R7.1, R11.1
/ATTENUATORS/AC_PATH: C5.1, K1.5
/ATTENUATORS/ATTEN_IN: K1.3; also elsewhere on the board
/ATTENUATORS/ATTEN_OUT: D4.1, D4.2, D5.1, D5.2, K2.6; also elsewhere on the board
/ATTENUATORS/DC_PATH: K1.2, K1.7
/RELAY_CTRL_0: Q3.1 (G); also elsewhere on the board
/RELAY_CTRL_1: Q2.1 (G); also elsewhere on the board
/RELAY_CTRL_2: Q1.1 (G); also elsewhere on the board
GND: C8.2, C9.2, C10.2, C11.2, C12.2, Q1.2 (S), Q2.2 (S), Q3.2 (S), R9.2, R11.2, R12.2, R13.2, TP3.1, TP4.1; also elsewhere on the board
unnamed: C5.2, K1.4
unnamed: C6.2, K3.2, R7.2
unnamed: C7.2, K3.4, R8.2
unnamed: D1.2 (A), K1.8, Q1.3 (D)
unnamed: D1.1 (K), R4.2
unnamed: D2.2 (A), K2.8, Q2.3 (D)
unnamed: D2.1 (K), R5.2
unnamed: D3.2 (A), K3.8, Q3.3 (D)
unnamed: D3.1 (K), R6.2
unnamed: K1.6, K2.3, TP1.1
unnamed: K2.5, R10.1, R13.1, TP2.1
unnamed: K2.7, K3.6

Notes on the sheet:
AC/DC Coupling
Decoupling Capacitors
INPUT COUPLING AND ATTENUATORS
Impedance Path Select



Board: 4 copper layers, 78.5 x 48.0 mm, 44 parts (19 on the bottom side), 29 nets.

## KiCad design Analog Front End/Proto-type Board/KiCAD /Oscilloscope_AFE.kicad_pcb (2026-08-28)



Board: 4 copper layers, 94.8 x 40.8 mm, 75 parts (16 on the bottom side), 45 nets.

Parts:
C1, C6, C7, C8, C16, C17, C18, C19, C20, C21, C22, C23: 0.1u; C_0603_1608Metric
C2, C3: 10p; C_0603_1608Metric
C4: 990p; C_0603_1608Metric
C5: 90p; C_0603_1608Metric
C9, C10, C11, C12, C13, C14, C15: 22u; C_1210_3225Metric_Pad1.33x2.70mm_HandSolder
C24, C27: 1u; C_0603_1608Metric
C25: 56p; C_0603_1608Metric
C26: 330p; C_0603_1608Metric
C28: 100p; C_0603_1608Metric
D1, D2, D3: 1N914WT; D_SOD-523
D4, D5: BAT54C; SOT-23
D6, D7: SZMMSZ5233BT1G; DIO_SZMMSZ5233BT1G
J1, J2: BNC; CONN_73100-0105_MOL
J3: Conn_02x08_Odd_Even; PinSocket_2x08_P2.54mm_Vertical
K1, K2, K3: G6J-2FL-Y DC5; RELAY_G6J-2FL-Y DC3_OMR
Q1, Q2, Q3: 2N7002; SOT-23
R1: 990k; R_0603_1608Metric
R2, R24, R25: 10k; R_0603_1608Metric
R3: 900k; R_0603_1608Metric
R4: 100k; R_0603_1608Metric
R5, R7: 75; R_0603_1608Metric
R6: 120; R_0603_1608Metric
R8, R9, R10: 5; R_0603_1608Metric
R11, R20: 1k; R_0603_1608Metric
R12, R16, R17, R18: 500k; R_0603_1608Metric
R13: 833k; R_0603_1608Metric
R14: 167k; R_0603_1608Metric
R15, R26: 80k; R_0603_1608Metric
R19: 30; R_0603_1608Metric
R21: 2k; R_0603_1608Metric
R22: 17.8k; R_0603_1608Metric
R23: 10M; R_0603_1608Metric
R27: 20k; R_0603_1608Metric
R28: 50; R_0603_1608Metric
U1, U2: OPA2140AIDGKR; DGK8
U3: BUF802IRGTR; VQFN16_RGT_TEX

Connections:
+1V_CLAMP: C24.2, D6.1, R11.2, U3.15 (CLH)
+5V: C6.1, C7.1, C8.1, C9.1, C10.1, C11.1, C12.1, C13.1, C16.1, C19.1, C22.1, C23.1, C27.2, D4.3, D7.1, J3.1, J3.3, J3.5, K1.1, K2.1, K3.1, R8.1, R9.1, R10.1, R11.1, R24.1, U1.8, U2.8, U3.1 (VS+), U3.12 (VSO+)
-1V_CLAMP: C27.1, D7.2, R20.1, U3.14 (CLL)
-5V: C14.1, C15.1, C17.1, C18.1, C20.1, C21.1, C24.1, D5.3, D6.2, J3.7, R20.2, U1.4, U2.4, U3.5 (VS-), U3.6 (AUX_BIAS), U3.8 (VS-__1), U3.10 (VSO-)
/Attenuators and Input Coupling/1MΩ Path: K2.2, K3.3
/Attenuators and Input Coupling/10:1 Attenuator: C3.1, C5.1, K3.5, R3.1, R4.1
/Attenuators and Input Coupling/50Ω Path: K2.4, R5.1, R6.2
/Attenuators and Input Coupling/100:1 Attenuator: C2.1, C4.1, K3.7, R1.1, R2.1
/Attenuators and Input Coupling/AC_PATH: C1.1, K1.5
/Attenuators and Input Coupling/ATTEN_OUT: D4.1, D4.2, D5.1, D5.2, K2.6, R13.1, R19.1
/Attenuators and Input Coupling/DC_PATH: K1.2, K1.7
/Attenuators and Input Coupling/IN: J1.1 (In), K1.3
/Attenuators and Input Coupling/RELAY_CTRL_0: J3.9, Q1.1 (G)
/Attenuators and Input Coupling/RELAY_CTRL_1: J3.11, Q2.1 (G)
/Attenuators and Input Coupling/RELAY_CTRL_2: J3.13, Q3.1 (G)
/JFET Buffer/BUFF_OUT: J2.1 (In), R28.2
/JFET Buffer/DC_OFFSET: J3.15, U2.5 (+)
GND: C4.2, C5.2, C6.2, C7.2, C8.2, C9.2, C10.2, C11.2, C12.2, C13.2, C14.2, C15.2, C16.2, C17.2, C18.2, C19.2, C20.2, C21.2, C22.2, C23.2, C28.1, J1.2 (Ext), J1.3, J2.2 (Ext), J2.3, J3.2, J3.4, J3.6, J3.8, J3.10, J3.12, J3.14, J3.16, Q1.2 (S), Q2.2 (S), Q3.2 (S), R2.2, R4.2, R5.2, R7.2, R14.2, R16.2, R22.2, R25.2, R27.2, U3.17 (EXP)
unnamed: C1.2, K1.4
unnamed: C2.2, K3.2, R1.2
unnamed: C3.2, K3.4, R3.2
unnamed: C25.2, R21.1, U1.1
unnamed: C26.1, R19.2
unnamed: D1.2 (A), K1.8, Q1.3 (D)
unnamed: D1.1 (K), R8.2
unnamed: D2.2 (A), K2.8, Q2.3 (D)
unnamed: D2.1 (K), R9.2
unnamed: D3.2 (A), K3.8, Q3.3 (D)
unnamed: D3.1 (K), R10.2
unnamed: K1.6, K2.3
unnamed: K2.5, R6.1, R7.1
unnamed: K2.7, K3.6
unnamed: R12.2, R15.2, U1.7
unnamed: R13.2, R14.1, U1.3 (+)
unnamed: C25.1, R15.1, R26.2, R27.1, U1.2 (-)
unnamed: R16.1, R17.2, U1.5 (+)
unnamed: R12.1, R18.2, U1.6 (-)
unnamed: R24.2, R25.1, U2.3 (+)
unnamed: R17.1, U2.1, U2.2 (-)
unnamed: R18.1, U2.6 (-), U2.7
unnamed: C26.2, R23.1, U3.2 (IN)
unnamed: C28.2, R21.2, U3.4 (IN_AUX)
unnamed: R23.2, U3.3 (IN_BIAS)
unnamed: R26.1, R28.1, U3.11 (OUT)
unnamed: R22.1, U3.7 (R_BIAS)

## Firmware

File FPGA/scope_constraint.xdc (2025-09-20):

## Clock: 100 MHz onboard oscillator
set_property PACKAGE_PIN W5 [get_ports clk]
set_property IOSTANDARD LVCMOS33 [get_ports clk]
create_clock -period 10.000 -name sys_clk_pin -waveform {0 5} [get_ports clk]

## Reset: BTN0
set_property PACKAGE_PIN U18 [get_ports i_reset]
set_property IOSTANDARD LVCMOS33 [get_ports i_reset]

## Timebase (5 switches: SW0–SW4)
set_property PACKAGE_PIN V17 [get_ports {i_timebase[0]}]
set_property IOSTANDARD LVCMOS33 [get_ports {i_timebase[0]}]

set_property PACKAGE_PIN V16 [get_ports {i_timebase[1]}]
set_property IOSTANDARD LVCMOS33 [get_ports {i_timebase[1]}]

set_property PACKAGE_PIN W16 [get_ports {i_timebase[2]}]
set_property IOSTANDARD LVCMOS33 [get_ports {i_timebase[2]}]

set_property PACKAGE_PIN W17 [get_ports {i_timebase[3]}]
set_property IOSTANDARD LVCMOS33 [get_ports {i_timebase[3]}]

set_property PACKAGE_PIN W15 [get_ports {i_timebase[4]}]
set_property IOSTANDARD LVCMOS33 [get_ports {i_timebase[4]}]

## Trigger type (SW5)
set_property PACKAGE_PIN V15 [get_ports i_trigger_type]
set_property IOSTANDARD LVCMOS33 [get_ports i_trigger_type]

## VGA RGB (12-bit)
set_property PACKAGE_PIN G19 [get_ports {RED[0]}]
set_property IOSTANDARD LVCMOS33 [get_ports {RED[0]}]

set_property PACKAGE_PIN H19 [get_ports {RED[1]}]
set_property IOSTANDARD LVCMOS33 [get_ports {RED[1]}]

set_property PACKAGE_PIN J19 [get_ports {RED[2]}]
set_property IOSTANDARD LVCMOS33 [get_ports {RED[2]}]

set_property PACKAGE_PIN N19 [get_ports {RED[3]}]
set_property IOSTANDARD LVCMOS33 [get_ports {RED[3]}]

set_property PACKAGE_PIN J17 [get_ports {GREEN[0]}]
set_property IOSTANDARD LVCMOS33 [get_ports {GREEN[0]}]

set_property PACKAGE_PIN H17 [get_ports {GREEN[1]}]
set_property IOSTANDARD LVCMOS33 [get_ports {GREEN[1]}]

set_property PACKAGE_PIN G17 [get_ports {GREEN[2]}]
set_property IOSTANDARD LVCMOS33 [get_ports {GREEN[2]}]

set_property PACKAGE_PIN D17 [get_ports {GREEN[3]}]
set_property IOSTANDARD LVCMOS33 [get_ports {GREEN[3]}]

set_property PACKAGE_PIN N18 [get_ports {BLUE[0]}]
set_property IOSTANDARD LVCMOS33 [get_ports {BLUE[0]}]

set_property PACKAGE_PIN L18 [get_ports {BLUE[1]}]
set_property IOSTANDARD LVCMOS33 [get_ports {BLUE[1]}]

set_property PACKAGE_PIN K18 [get_ports {BLUE[2]}]
set_property IOSTANDARD LVCMOS33 [get_ports {BLUE[2]}]

set_property PACKAGE_PIN J18 [get_ports {BLUE[3]}]
set_property IOSTANDARD LVCMOS33 [get_ports {BLUE[3]}]

## VGA Syncs
set_property PACKAGE_PIN P19 [get_ports H_SYNC]
set_property IOSTANDARD LVCMOS33 [get_ports H_SYNC]

set_property PACKAGE_PIN R19 [get_ports V_SYNC]
set_property IOSTANDARD LVCMOS33 [get_ports V_SYNC]
